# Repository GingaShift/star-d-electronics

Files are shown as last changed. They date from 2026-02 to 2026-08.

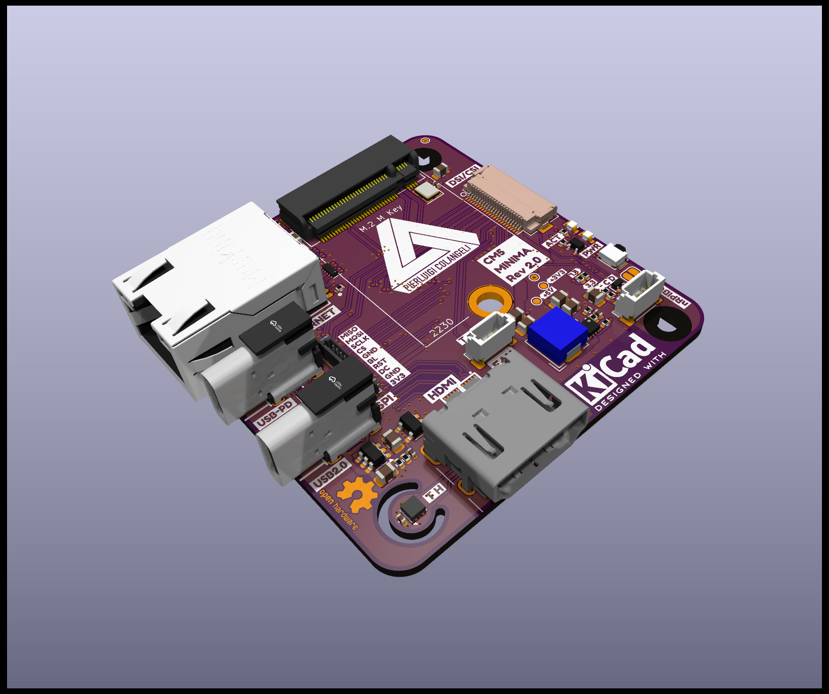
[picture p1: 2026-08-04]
AUTRE/CM5_MINIMA_REV2-main/CM5_MINIMA_REV2-main/PICS/SIDE.png

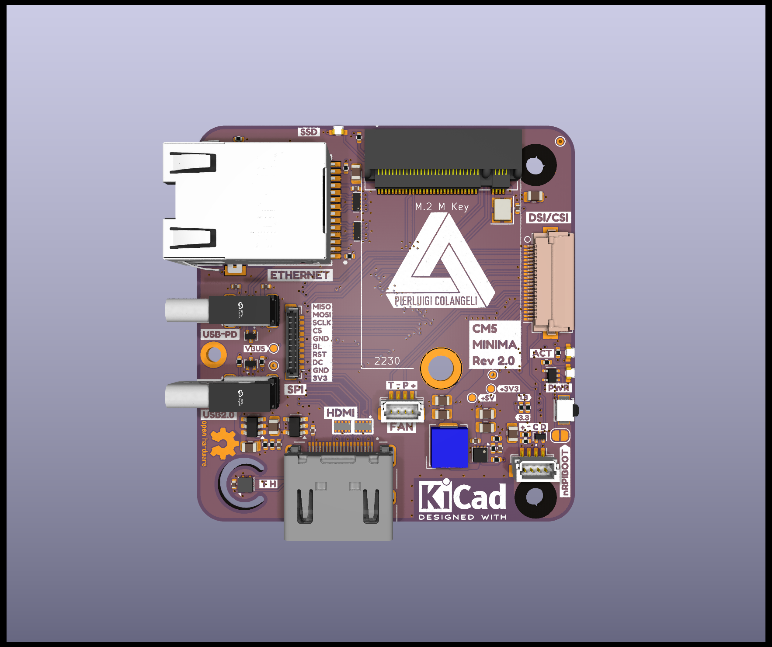
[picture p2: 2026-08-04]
AUTRE/CM5_MINIMA_REV2-main/CM5_MINIMA_REV2-main/PICS/F.png

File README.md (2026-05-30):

# STAR-D Electronics

Electronics repository for the STAR-D (Space Test of Amoeba Response - Dictyostelium) experiment developed within the ESA REXUS/BEXUS programme.

The electronics architecture is divided into several dedicated boards responsible for power conversion, experiment control, imaging, sensing, actuation and illumination.

---

# System Overview

The STAR-D electronics system is organized around:

- Power Board
- Main Control Board
- 5V Distribution Board
- CM5 Imaging System
- Microscope LED Board
- External Sensor Interfaces

---

# Power Board

## Purpose

Interfaces directly with the REXUS Service Module.

Responsibilities:

- 28V input from REXUS
- Power conversion
- Signal isolation
- RS422 communications
- Power distribution to the experiment

## PCB

Power_Board_F
Power_Board_B

## Main Components

- DC/DC Converters
- Optocouplers
- RS422 Transceiver
- D-SUB Interface
- Protection circuitry

---

# Main Control Board

## Purpose

Central controller of the experiment.

Responsibilities:

- Sensor acquisition
- Heater control
- Fluidic control
- Experiment sequencing
- Telemetry generation

## PCB

Main_Board
Main_Board_B

## Main Components

- ESP32-S3
- MAX31865
- PT100 Interface
- LSM6DSM
- ABP Pressure Sensor Interface
- SLF3S Flow Sensor Interface
- Actuator Drivers

---

# 5V Distribution Board

## Purpose

Dedicated power distribution board for high-current 5V subsystems.

Responsibilities:

- CM5 power supply

## PCB

5V_Board_F
5V_Board_B

---

# CM5 Imaging System

## Purpose

Scientific image acquisition and storage.

Responsibilities:

- Microscope control
- Camera acquisition
- Data storage
- Image processing

## PCB



## Main Components

- Raspberry Pi CM5
- NVMe SSD
- CSI Camera Interface

---

# Microscope LED PCB

## Purpose

Microscope illumination.

Responsibilities:

- Brightfield illumination
- Fluorescence illumination

## PCB

M_led

---

# External BME280 Board

## Purpose

Environmental monitoring outside the Pressure Vessel.

## PCB

External_BME_F
External_BME_B

---

# Repository Structure

```text
Documentation/
├── SED
├── Part_Listing
├── ICD
└── Images

Power_Board/

Main_Board/

5V_Board/

CM5_System/

Microscope_LED_PCB/

BME280_External/
```

---

# Documentation

Useful documents:

- STAR-D SED
- REXUS ICD
- Global Part Listing
- Power Board Part Listing
- Test Reports
- Integration Documents

---

# Team

STAR-D Electronics Team

Electronic Lead:
**Eden Elfassy**

ESA REXUS/BEXUS Programme

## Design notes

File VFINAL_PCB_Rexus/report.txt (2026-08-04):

Fichier placement: 'C:\Users\elfde\Desktop\STAR-D ELECTRONICS\VFINAL_PCB_Rexus\Main_PCB_STAR_D-all-pos.csv'.
Info: Nombre de composants: 120.
Info: Fini.

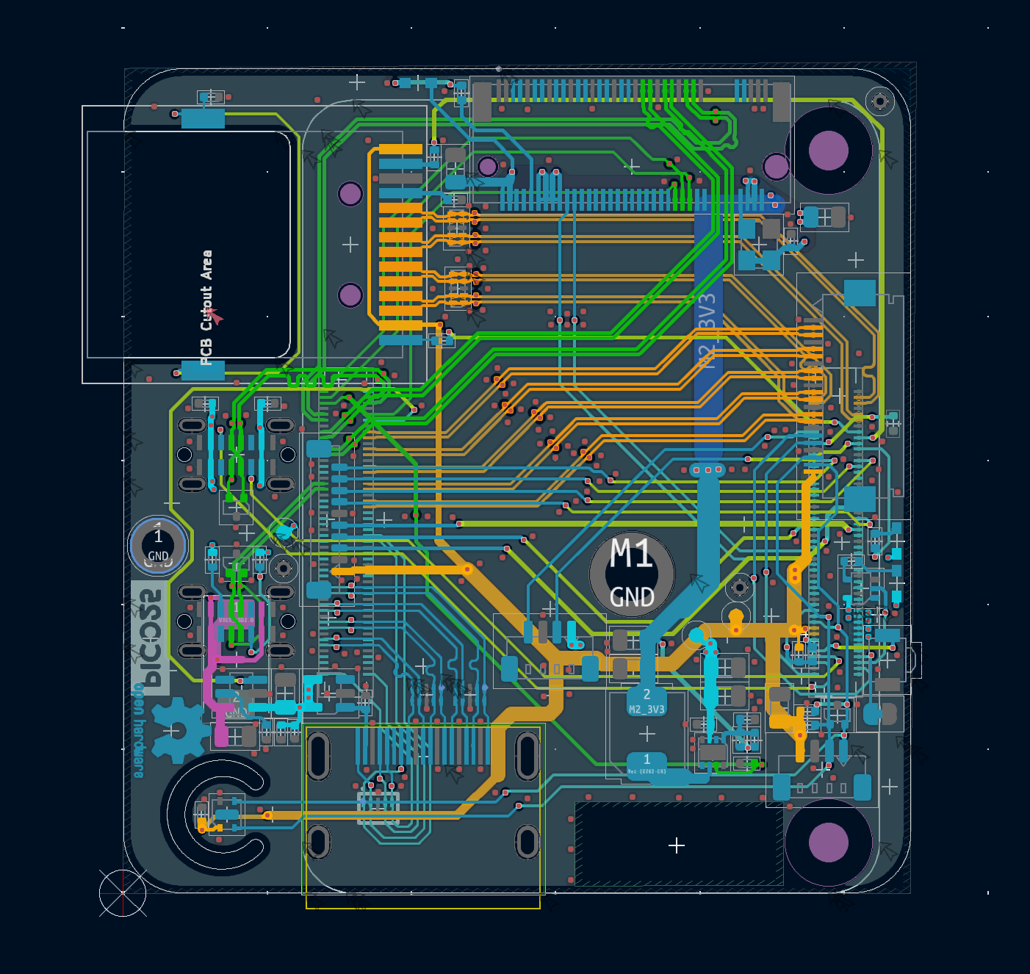
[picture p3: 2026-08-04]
AUTRE/CM5_MINIMA_REV2-main/CM5_MINIMA_REV2-main/PICS/PCB.png

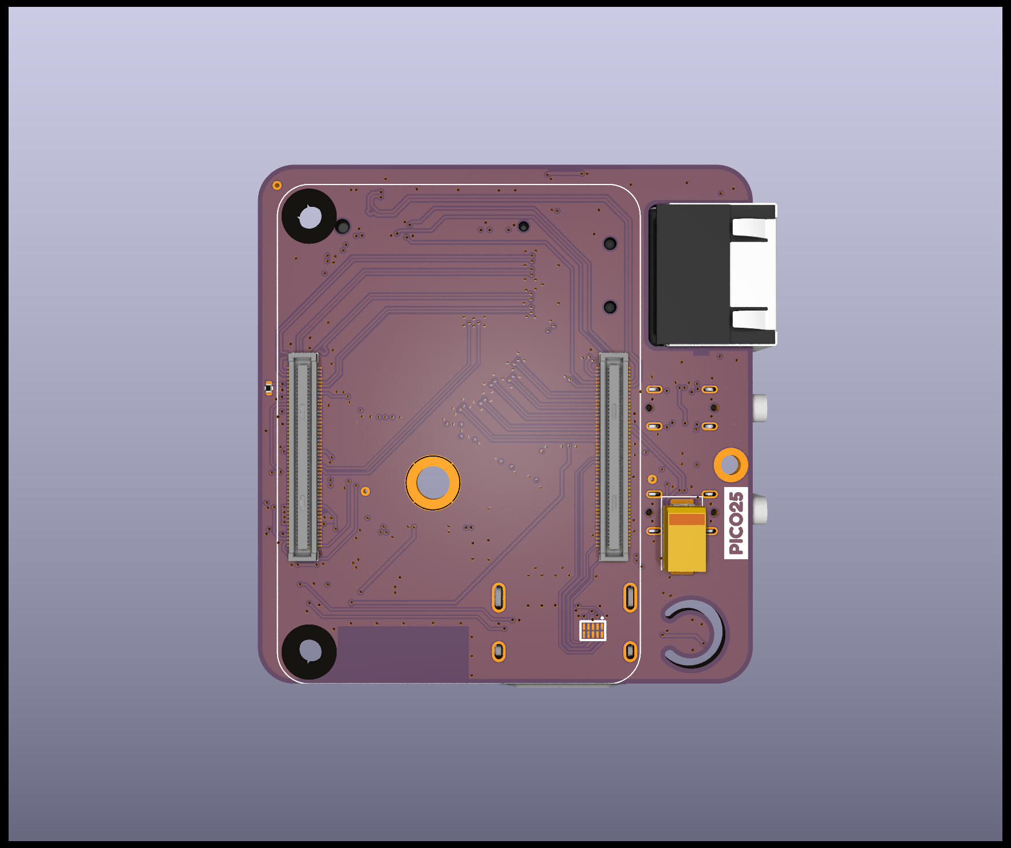
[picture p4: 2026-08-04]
AUTRE/CM5_MINIMA_REV2-main/CM5_MINIMA_REV2-main/PICS/B.png

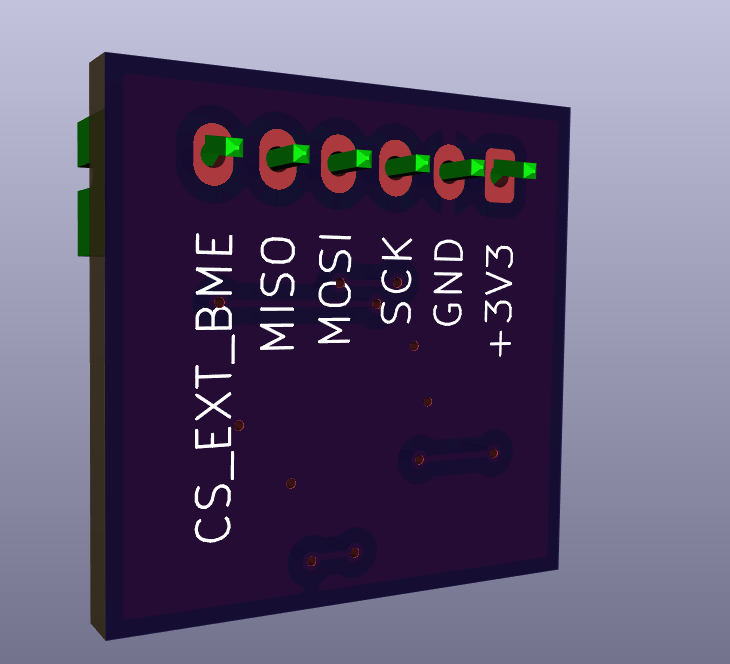
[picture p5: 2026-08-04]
Pics PCBs/External_BME_B.png

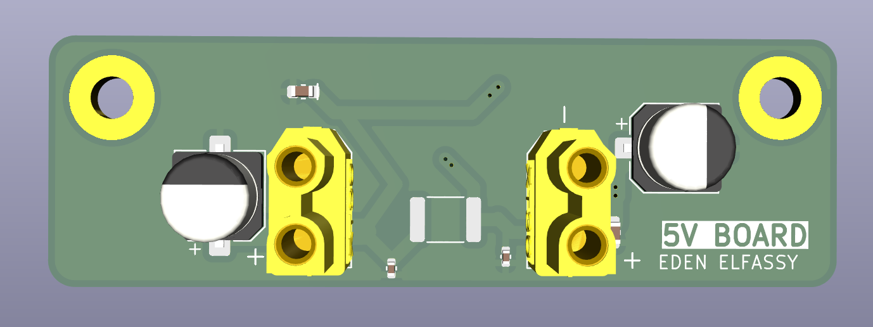
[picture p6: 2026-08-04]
Pics PCBs/5V_Board_F.png

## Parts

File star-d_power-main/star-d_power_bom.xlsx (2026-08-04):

Reference | Qty | Value | Footprint | Manufacturer Name | Comment
C1_1,C1_2,C1_3,C1_4,C1_5,C1_6,C1_7,C1_8,C1_9,C1_10,C1_11,C1_12,C1_13,C1_14,C1_15,C1_16,C1_17,C1_18 | 18 | 4.7uF | Capacitor_SMD:C_1206_3216Metric | Murata | GRM31CR71H475KA12L
C2_1,C2_2,C2_3 | 3 | 8200pF | Capacitor_SMD:C_0603_1608Metric | Vishay | VJ0603Y822KXAAC
C3_1,C3_2,C3_3 | 3 | 4.7uF | Capacitor_SMD:C_0603_1608Metric | Murata | GRM188Z71A475ME15D
C4_1,C4_2,C4_3,CD_1,CD_2 | 5 | 100nF | Capacitor_SMD:C_0603_1608Metric | KEMET | C0603C104K3RAC7411
C5_1,C5_2,C5_3,C5_4,C5_5,C5_6 | 6 | 47uF | Capacitor_SMD:C_1210_3225Metric | Murata | GRM32ER71A476KE15L
C5_7,C5_8,C5_9 | 3 | 47uF | Capacitor_SMD:C_2220_5750Metric | TDK | CGA9N3X7R1E476M230KB
CF1 | 1 | 1uF | Capacitor_SMD:C_1206_3216Metric | TDK | C3216X7R1H105K160AB
CFT1,CFT2,CFT3,CFT4 | 4 | C_Feedthrough | NFM18CC221R1C3D:NFM18CC101R1C3D | Murata | NFM18CC221R1C3D
D1,D2,D3 | 3 | LED | LED_SMD:LED_0603_1608Metric | LITEON | LTST-C191KFKT
FL1 | 1 | Common Mode Choke 215uH | PA2754NL:PA2754NL | Pulse Electronics | PA2754NL
IC1,IC2,IC3 | 3 | MAX17639AFN+ | MAX17639AFN+:MAX17793AFN | Analog Devices | MAX17639AFN+
J1 | 1 | 3.3V connector | Connector_AMASS:AMASS_XT30PW-F_1x02_P2.50mm_Horizontal | AMASS | XT30PW-F
J2 | 1 | 5V connector | Connector_AMASS:AMASS_XT30PW-F_1x02_P2.50mm_Horizontal | AMASS | XT30PW-F
J3 | 1 | 7V connector | Connector_AMASS:AMASS_XT30PW-F_1x02_P2.50mm_Horizontal | AMASS | XT30PW-F
J4 | 1 | D-sub input | LD15P33E4GX00LF:AMPHENOL_LD15P33E4GX00LF | Amphenol | LD15P33E4GX00LF
J5 | 1 | D-sub output | LD15P33E4GX00LF:AMPHENOL_LD15P33E4GX00LF | Amphenol | LD15P33E4GX00LF
L1_1 | 1 | 2.2uH | XGL1010-222MED:IND_XGL1010-222MED | Coilcraft | XGL1010-222MED
L1_2,L1_3 | 2 | 3.3uH | XGL1010-222MED:IND_XGL1010-222MED | Coilcraft | XGL1010-332MED
LF1 | 1 | 100uH | SRP2313AA-101M:INDPM235220X1300N | Bourns | SRP2313AA-101M
R1_1,R1_2,R1_3 | 3 | 3.32M | Resistor_SMD:R_0603_1608Metric | Vishay | CRCW06033M32FKEA
R2_1 | 1 | 1.5M | Resistor_SMD:R_0603_1608Metric | Vishay | CRCW06031M50FKEA
R2_2 | 1 | 825k | Resistor_SMD:R_0603_1608Metric | Vishay | CRCW0603825KFKEA
R2_3 | 1 | 604k | Resistor_SMD:R_0603_1608Metric | Vishay | CRCW0603604KFKEA
R3_1 | 1 | 158k | Resistor_SMD:R_0603_1608Metric | Vishay | CRCW0603158KFKEA
R3_2 | 1 | 249k | Resistor_SMD:R_0603_1608Metric | Vishay | CRCW0603249KFKEA
R3_3 | 1 | 105k | Resistor_SMD:R_0603_1608Metric | Vishay | CRCW0603105KFKEA
R4_1 | 1 | 34.8k | Resistor_SMD:R_0603_1608Metric | Vishay | CRCW060334K8FKEA
R4_2 | 1 | 34k | Resistor_SMD:R_0603_1608Metric | Vishay | CRCW060334K0FKEA
R4_3 | 1 | 9.76k | Resistor_SMD:R_0603_1608Metric | Vishay | CRCW06039K76FKEA
R5_1,R5_2,R5_3 | 3 | 75k | Resistor_SMD:R_0603_1608Metric | Vishay | CRCW060375K0FKEA
R6_1,R6_2,R6_3 | 3 | 20k | Resistor_SMD:R_0603_1608Metric | Vishay | CRCW060320K0FKEA
RLED_1,RO1,RO3,RO5 | 4 | 1k | Resistor_SMD:R_0603_1608Metric | Panasonic | ERJ-PA3J102V
RLED_2 | 1 | 604R | Resistor_SMD:R_0603_1608Metric | Panasonic | ERJ-PA3D6040V
RLED_3 | 1 | 261R | Resistor_SMD:R_0603_1608Metric | Panasonic | ERJ-PA3F2610V
RO2,RO4,RO6 | 3 | 3k3 | Resistor_SMD:R_0603_1608Metric | Panasonic | ERJ-PA3J332V
U1,U2,U3 | 3 | VO615A-4 | Package_DIP:DIP-4_W10.16mm | Vishay | VO615A-4
U4 | 1 | BME280 | Package_LGA:Bosch_LGA-8_2.5x2.5mm_P0.65mm_ClockwisePinNumbering | Bosch | BME280

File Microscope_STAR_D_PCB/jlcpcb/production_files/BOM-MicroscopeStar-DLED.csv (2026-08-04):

Comment | Designator | Footprint | LCSC | Quantity
180R | R1,R2,R3,R4 | R_0402_1005Metric | C138045 | 4
Conn_01x03_Socket | J1 | Molex_Micro-Fit_3.0_43650-0312_1x03-1MP_P3.00mm_Horizontal | C114109 | 1
KT-0603-W | D1,D2,D3,D4 | LED_0603_1608Metric | C5973179 | 4
SI2302B-TP | Q1 | SOT95P237X125-3N | C52117627 | 1

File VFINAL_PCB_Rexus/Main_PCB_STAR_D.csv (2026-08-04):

Reference | Qty | Value | DNP | Exclude from BOM | Exclude from Board | Footprint | Datasheet
AE1 | 1 | Antenna_Chip |  |  |  | Connector_Coaxial:U.FL_Molex_MCRF_73412-0110_Vertical
C1,C6,C10 | 3 | 1uF 0402 |  |  |  | Capacitor_SMD:C_0402_1005Metric
C2,C4 | 2 | 12pF 0402 |  |  |  | Capacitor_SMD:C_0402_1005Metric
C3 | 1 | 10uF 0402 |  |  |  | Capacitor_SMD:C_0402_1005Metric
C5,C7,C9,C15,C17,C18,C19,C20,C21,C22,C24,C27,C30,C33,C34,C35 | 16 | 100nF 0402 |  |  |  | Capacitor_SMD:C_0402_1005Metric
C8 | 1 | 10nF 0402 |  |  |  | Capacitor_SMD:C_0402_1005Metric
C11,C13 | 2 | 0.1uF 0402 |  |  |  | Capacitor_SMD:C_0402_1005Metric
C12 | 1 | 10nF 0603 |  |  |  | Capacitor_SMD:C_0402_1005Metric
C14 | 1 | 15pF 0402 |  |  |  | Capacitor_SMD:C_0402_1005Metric
C16 | 1 | 2.2uF 0603 |  |  |  | Capacitor_SMD:C_0402_1005Metric
C23,C28,C31,C32 | 4 | 10uF 0603 |  |  |  | Capacitor_SMD:C_0603_1608Metric
C25,C26 | 2 | 0.1uF |  |  |  | Capacitor_SMD:C_0402_1005Metric
C29 | 1 | 100nF |  |  |  | Capacitor_SMD:C_0402_1005Metric
D1 | 1 | MBR0520 |  |  |  | Diode_SMD:D_SOD-123 | http://www.mccsemi.com/up_pdf/MBR0520~MBR0580(SOD123).pdf
D2,D3,D4 | 3 | KT-0805Y |  |  |  | LED_SMD:LED_0805_2012Metric
IC1 | 1 | MAX31865ATP+ |  |  |  | MAX31865ATP+:QFN65P500X500X80-21N | https://www.analog.com/MAX31865/datasheet
IC2 | 1 | W25Q01JVZEIQ |  |  |  | Package_SON:WSON-8-1EP_6x5mm_P1.27mm_EP3.4x4.3mm | https://www.winbond.com/hq/search-resource-file.jsp?partNo=W25Q01JVZEIQ&type=datasheet
IC3 | 1 | ISL83491IBZ-T |  |  |  | ISL83491IBZ-T:SOIC127P600X175-14N | https://www.renesas.com/en-us/www/doc/datasheet/isl83483-85-88-90-91.pdf
IC4 | 1 | DRV8834PWP |  |  |  | DRV8834PWP:SOP65P640X120-25N | https://datasheet.datasheetarchive.com/originals/distributors/Datasheets-SFU2/DSASFU100034685.pdf
IC5 | 1 | ULN2003ADR |  |  |  | ULN2003ADR:SOIC127P600X175-16N | http://www.ti.com/lit/ds/symlink/uln2003a.pdf
J1 | 1 | Conn_01x05_Pin |  |  |  | Connector_JST:JST_EH_S5B-EH_1x05_P2.50mm_Horizontal
J2 | 1 | Conn_01x09 |  |  |  | Connector_JST:JST_GH_BM09B-GHS-TBT_1x09-1MP_P1.25mm_Vertical
J3 | 1 | Conn_01x04_Pin |  |  |  | Connector_JST:JST_EH_S4B-EH_1x04_P2.50mm_Horizontal
J4,J7 | 2 | Conn_01x06_Pin |  |  |  | Connector_JST:JST_EH_S6B-EH_1x06_P2.50mm_Horizontal
J5 | 1 | Conn_01x04 |  |  |  | Connector_JST:JST_PH_S4B-PH-K_1x04_P2.00mm_Horizontal
J6,J12,J13,J15,J_HEATER1,J_HEATER2,J_HEATER3,J_HEATER4 | 8 | Conn_01x02_Pin |  |  |  | Connector_AMASS:AMASS_XT30U-F_1x02_P5.0mm_Vertical
J8 | 1 | Conn_01x02 |  |  |  | Connector_JST:JST_EH_S2B-EH_1x02_P2.50mm_Horizontal
J9 | 1 | Conn_01x05 |  |  |  | Connector_JST:JST_XH_B5B-XH-A_1x05_P2.50mm_Vertical
J10 | 1 | TYPE-C 16PIN 2MD(073) |  |  |  | Connector_USB:USB_C_Receptacle_GCT_USB4105-xx-A_16P_TopMnt_Horizontal | https://www.usb.org/sites/default/files/documents/usb_type-c.zip
J11 | 1 | Conn_01x03 |  |  |  | Connector_JST:JST_EH_S3B-EH_1x03_P2.50mm_Horizontal
L1 | 1 | 2.0nH 0402 |  |  |  | Inductor_SMD:L_0402_1005Metric
L3 | 1 | 4.7nH 0402 |  |  |  | Inductor_SMD:L_0402_1005Metric
Q7,Q8,Q9,Q10 | 4 | IRLML6344TRPBF |  |  |  | IRLML6344TRPBF:SOT95P237X112-3N | https://www.infineon.com/dgdl/irlml6344pbf.pdf?fileId=5546d462533600a4015356689c44262c
R1,R5,R12 | 3 | 10kR 0402 |  |  |  | Resistor_SMD:R_0402_1005Metric
R2 | 1 | 2R 0402 |  |  |  | Resistor_SMD:R_0402_1005Metric
R3 | 1 | 47kR 0402 |  |  |  | Resistor_SMD:R_0402_1005Metric
R4,R_ADC_POT1 | 2 | 1kR 0402 |  |  |  | Resistor_SMD:R_0402_1005Metric
R6,R8 | 2 | 51kR 0402 |  |  |  | Resistor_SMD:R_0402_1005Metric
R7 | 1 | 400R 0402 |  |  |  | Resistor_SMD:R_0402_1005Metric
R9,R11 | 2 | 0.2R 1206 |  |  |  | Resistor_SMD:R_0402_1005Metric
R10 | 1 | 120R 0402 |  |  |  | Resistor_SMD:R_0402_1005Metric
R13 | 1 | 22kR 0402 |  |  |  | Resistor_SMD:R_0402_1005Metric
R14,R15 | 2 | 5.1kR 0402 |  |  |  | Resistor_SMD:R_0402_1005Metric
R16,R17 | 2 | 22R 0402 |  |  |  | Resistor_SMD:R_0402_1005Metric
R18,R19 | 2 | 2kR 0402 |  |  |  | Resistor_SMD:R_0402_1005Metric
R_G1,R_G2,R_G3,R_G4 | 4 | 100R 0402 |  |  |  | Resistor_SMD:R_0402_1005Metric
R_I2C_SCL1,R_I2C_SCL2 | 2 | 4K7 0402 |  |  |  | Resistor_SMD:R_0402_1005Metric
R_PD1,R_PD2,R_PD3,R_PD4 | 4 | 100kR 0402 |  |  |  | Resistor_SMD:R_0402_1005Metric
SW1,SW2 | 2 | SW_SPST |  |  |  | Button_Switch_SMD:SW_Tactile_SPST_NO_Straight_CK_PTS636Sx25SMTRLFS
TP1,TP2,TP3,TP4,TP5,TP6,TP7,TP8,TP9,TP10,TP11,TP12,TP13,TP14,TP15,TP16,TP18 | 17 | TestPoint |  |  |  | TestPoint:TestPoint_Pad_1.0x1.0mm
U1 | 1 | ESP32-S3 |  |  |  | Package_DFN_QFN:QFN-56-1EP_7x7mm_P0.4mm_EP4x4mm | https://www.espressif.com/sites/default/files/documentation/esp32-s3_datasheet_en.pdf
U2 | 1 | BME280 |  |  |  | Package_LGA:Bosch_LGA-8_2.5x2.5mm_P0.65mm_ClockwisePinNumbering | https://www.bosch-sensortec.com/media/boschsensortec/downloads/datasheets/bst-bme280-ds002.pdf
U4 | 1 | LSM6DSM |  |  |  | Package_LGA:LGA-14_3x2.5mm_P0.5mm_LayoutBorder3x4y | https://www.st.com/resource/en/datasheet/lsm6dsm.pdf
Y1 | 1 | 40MHz 3225 9pF |  |  |  | Crystal:Crystal_SMD_3225-4Pin_3.2x2.5mm

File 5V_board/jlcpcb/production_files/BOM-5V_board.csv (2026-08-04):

Comment | Designator | Footprint | LCSC | Quantity
100nF 0402 | C33,C34 | C_0402_1005Metric | C307331 | 2
10uF 0603 | C31,C32 | C_0603_1608Metric | C96446 | 2
470µF | C35,C_CM5_BULK1 | CP_Elec_6.3x7.7 | C3354 | 2
Conn_01x02_Pin | J13,J15 | Molex_Micro-Fit_3.0_43650-0215_1x02_P3.00mm_Vertical | C293740 | 2
Conn_01x04 | J1 | Molex_Micro-Latch_53253-0470_1x04_P2.00mm_Vertical | C504808 | 1

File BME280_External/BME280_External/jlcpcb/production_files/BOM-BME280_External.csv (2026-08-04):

Comment | Designator | Footprint | LCSC | Quantity
0.1uF | C1,C2 | C_0402_1005Metric | C141382 | 2
BME280 | U1 | Bosch_LGA-8_2.5x2.5mm_P0.65mm_ClockwisePinNumbering | C92489 | 1
Conn_01x06_Pin | J1 | Molex_Micro-Latch_53253-0670_1x06_P2.00mm_Vertical | C564034 | 1

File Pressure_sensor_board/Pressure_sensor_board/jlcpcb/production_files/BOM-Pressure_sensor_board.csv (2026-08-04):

Comment | Designator | Footprint | LCSC | Quantity
100nF 0603 | C1 | C_0603_1608Metric | C24452 | 1
Conn_01x05 | J1 | Molex_Micro-Latch_53254-0570_1x05_P2.00mm_Horizontal | C585950 | 1
ABPDANV015PGSA3 | IC1 | ABPDANV015PGSA3 |  | 1

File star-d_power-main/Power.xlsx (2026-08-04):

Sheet: Folha1
VIN | 28 | V |  | D | 0.25
VOUT | 7 | V |  | CIN | 49.34210526 | uF
fSW | 400000 | Hz |  | L | 3.645833333 | uH |  | LSEL | 6.8 | uH
DeltaVIN | 0.1 | V |  | tresponse | 7e-06
eff | 0.95 |  |  | COUT | 87.5 | uF |  | COUTSEL | 111 | uF
IOUTMAX | 10 | A |  | CSS | 8200 | pF
K | 4.8 |  |  | RUVLBOT | 605.8394161 | kR
fc | 50000 | Hz |  | RFBTOP | 104.1441441 | kR | 104
ISTEP | 5 | A |  | RFBBOT | 9.763513514 | kR
DeltaVOUT | 0.2 | V
RUVLTOP | 3.32 | MR
VENR | 1.25 | V |  | RFBTOP | 105
VINU | 8.1 | V |  | RFBBOT | 9.76
 |  |  |  | VOUT | 7.054918033
 |  |  |  |  | 98.34 | 158 | 1.606670734
 |  |  |  |  | 134.16 | 249 | 1.855992844
 |  |  |  |  | 104 | 176.8
 |  |  | 3.142857143 |  | 33.81147541

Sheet: Folha2
Designator | Amount | R/L/C | V min | Others | Component | Size | Link | Price/un | Total/PCB
IC[1..3] | 3 |  |  |  | MAX17639AFN+ |  | https://www.mouser.fr/ProductDetail/Analog-Devices-Maxim-Integrated/MAX17639AFN+ | 8.13 € | 80.15 €
R1_[1..3] | 3 | 3.32 Mohm |  |  | CRCW06033M32FKEA | 0603 | https://www.mouser.fr/ProductDetail/Vishay/CRCW06033M32FKEA | 0.09 €
R2_1 | 1 | 1.5 Mohm |  |  | CRCW06031M50FKEA | 0603 | https://www.mouser.fr/ProductDetail/Vishay/CRCW06031M50FKEA | 0.09 €
R2_2 | 1 | 825 kohm |  |  | CRCW0603825KFKEA | 0603 | https://www.mouser.fr/ProductDetail/Vishay/CRCW0603825KFKEA?qs=p2bJuJLPpvQJv%252BSX6BCMUg%3D%3D | 0.09 €
R2_3 | 1 | 604 kohm |  |  | CRCW0603604KFKEA | 0603 | https://www.mouser.fr/ProductDetail/Vishay/CRCW0603604KFKEA?qs=ze%252BM7jRK1VYKCr%2Fok50BCw%3D%3D | 0.09 €
R3_1 | 1 | 158 kohm |  |  | CRCW0603158KFKEA | 0603 | https://www.mouser.fr/ProductDetail/Vishay/CRCW0603158KFKEA?qs=5N7VPDfziMSpEbCL%252B8rPOw%3D%3D | 0.09 €
R3_2 | 1 | 249 kohm |  |  | CRCW0603249KFKEA | 0603 | https://www.mouser.fr/ProductDetail/Vishay/CRCW0603249KFKEA?qs=mhqxD2tmD97uUS1nIJhakQ%3D%3D | 0.09 €
R3_3 | 1 | 105 kohm |  |  | CRCW0603105KFKEA | 0603 | https://www.mouser.fr/ProductDetail/Vishay/CRCW0603105KFKEA?qs=l1I5L%2FyVolijl%252Bqg9cSIKQ%3D%3D | 0.09 €
R4_1 | 1 | 34.8 kohm |  |  | CRCW060334K8FKEA | 0603 | https://www.mouser.fr/ProductDetail/Vishay/CRCW060334K8FKEA?qs=68g8TF7PocIAjJxcXJVf9g%3D%3D | 0.09 €
R4_2 | 1 | 34 kohm |  |  | CRCW060334K0FKEA | 0603 | https://www.mouser.fr/ProductDetail/Vishay/CRCW060334K0FKEA?qs=9%2FCyznrMg3XHBoGG%2FQg7oQ%3D%3D | 0.09 €
R4_3 | 1 | 9.76 kohm |  |  | CRCW06039K76FKEA | 0603 | https://www.mouser.fr/ProductDetail/Vishay/CRCW06039K76FKEA?qs=yf2sAwiRN649TjJ%2FhlEI1Q%3D%3D | 0.09 €
R5_[1..3] | 3 | 75 kohm |  |  | CRCW060375K0FKEA | 0603 | https://www.mouser.fr/ProductDetail/Vishay/CRCW060375K0FKEA?qs=rTzW0HAgjYM2sBnUIlegvw%3D%3D | 0.09 €
R6_[1..3] | 3 | 20 kohm |  |  | CRCW060320K0FKEA | 0603 | https://www.mouser.fr/ProductDetail/Vishay/CRCW060320K0FKEA?qs=QZuYiDxzHajCQLs7n6RwKw%3D%3D | 0.09 €
RLED_1 | 1 | 1 kohm |  |  | ERJ-PA3J102V | 0603 | https://www.mouser.fr/ProductDetail/Panasonic/ERJ-PA3J102V?qs=BzJM0faLVqWUoK2brnXytQ%3D%3D | 0.10 €
RLED_2 | 1 | 604 ohm |  |  | ERJ-PA3D6040V | 0603 | https://www.mouser.fr/ProductDetail/Panasonic/ERJ-PA3D6040V?qs=BzJM0faLVqVr6j5%252BuCH0wQ%3D%3D | 0.21 €
RLED_3 | 1 | 261 ohm |  |  | ERJ-PA3F2610V | 0603 | https://www.mouser.fr/ProductDetail/Panasonic/ERJ-PA3F2610V?qs=BzJM0faLVqWOtl0KpXWkew%3D%3D | 0.12 €
L1 | 1 | 2.2 uH | 3.3V |  | XGL1010-222MED |  | https://www.digikey.fr/en/products/detail/coilcraft/XGL1010-222MED/21387621?s=N4IgTCBcDaIBoHEAyBGADOgtGHBZAogCIgC6AvkA | 5.82 €
L[2,3] | 2 | 3.3 uH | 7V |  | XGL1010-332MED |  | https://www.digikey.fr/en/products/detail/coilcraft/XGL1010-332MED/21387582?s=N4IgTCBcDaIBoHEAyBGADOgtAZm2AsgKIAiIAugL5A | 5.82 €
C1_[1..18] | 18 | 4.7 uF | 28V | X7R | GRM31CR71H475KA12L | 1206 | https://www.digikey.de/de/products/detail/murata-electronics/GRM31CR71H475KA12L/2548209 | 0.27 €
C2_[1..3] | 3 | 8200 pF |  | X7R | VJ0603Y822KXAAC | 0603 | https://www.mouser.fr/ProductDetail/Vishay-Vitramon/VJ0603Y822KXAAC?qs=sGAEpiMZZMvsSlwiRhF8qsy6D4RIz3svHH6F26SGKQI%3D | 0.15 €
C3_[1..3] | 3 | 4.7 uF | 1.8V | X7R | GRM188Z71A475ME15D | 0603 | https://www.digikey.de/de/products/detail/murata-electronics/GRM188Z71A475ME15D/13904814 | 0.19 €
C4_[1..3], CD_[1,2] | 5 | 100 nF |  | X7R | C0603C104K3RAC7411 | 0603 | https://www.mouser.fr/ProductDetail/KEMET/C0603C104K3RAC7411?qs=sGAEpiMZZMvsSlwiRhF8qtMAW1uaXrptnL6k6SP7Y74%3D | 0.09 €
C5_[1..6] | 6 | 47 uF | 5V | X7R | GRM32ER71A476KE15L | 1210 | https://www.digikey.be/de/products/detail/murata-electronics/GRM32ER71A476KE15L/2039039 | 0.72 €
C5_[7..9] | 3 | 47 uF | 12V | X7R | CGA9N3X7R1E476M230KB | 2220 | https://www.mouser.de/ProductDetail/TDK/CGA9N3X7R1E476M230KB | 3.78 €
D[1..3] | 3 |  |  | LED | LTST-C191KFKT | 0603 | https://www.mouser.fr/ProductDetail/LITEON/LTST-C191KFKT?qs=sGAEpiMZZMv0DJfhVcWlKzPaVbnPffcwrhTtPymJX2Y%3D | 0.09 €
J[1..3] | 3 |  |  | horizontal power | 43650-0200 |  | https://www.mouser.fr/ProductDetail/Molex/43650-0200?qs=HlEFOAM0q6XGaAJJj3Pssw%3D%3D | 0.92 €
J4 | 1 |  |  | Dsub-15, right-angle, male | LD15P33E4GX00LF |  | https://www.mouser.fr/ProductDetail/Amphenol-Commercial-Products/LD15P33E4GX00LF?qs=tZOhSuJQg1lUHGna%252BrXX2w%3D%3D | 1.61 €
J5 | 1 |  |  | Dsub-15, right-angle, female | LD15S33E4GV00LF |  | https://www.mouser.fr/ProductDetail/Amphenol-Commercial-Products/LD15S33E4GV00LF?qs=tZOhSuJQg1mwdHXzYsS27Q%3D%3D | 1.74 €
FL1 | 1 | 215uH |  | CMC | PA2754NL |  | https://www.mouser.fr/ProductDetail/Pulse-Electronics/PA2754NL?qs=%252BUGZmmosPSIl0ME75doAGQ%3D%3D | 1.78 €
LF1 | 1 | 100uH |  |  | SRP2313AA-101M |  | https://www.mouser.fr/ProductDetail/Bourns/SRP2313AA-101M?qs=gZXFycFWdANfITbqx%252BPtOw%3D%3D | 5.67 €
CF1 | 1 | 1uF |  |  | C3216X7R1H105K160AB | 1206 | https://www.mouser.fr/ProductDetail/TDK/C3216X7R1H105K160AB | 0.10 €
CFT[1..4] | 4 | 220pF |  | feed-through | NFM18CC221R1C3D | 0603 | https://www.mouser.fr/ProductDetail/Murata-Electronics/NFM18CC221R1C3D?qs=0j%2FqW2fzXq8leLhxLw8kvg%3D%3D | 0.11 €

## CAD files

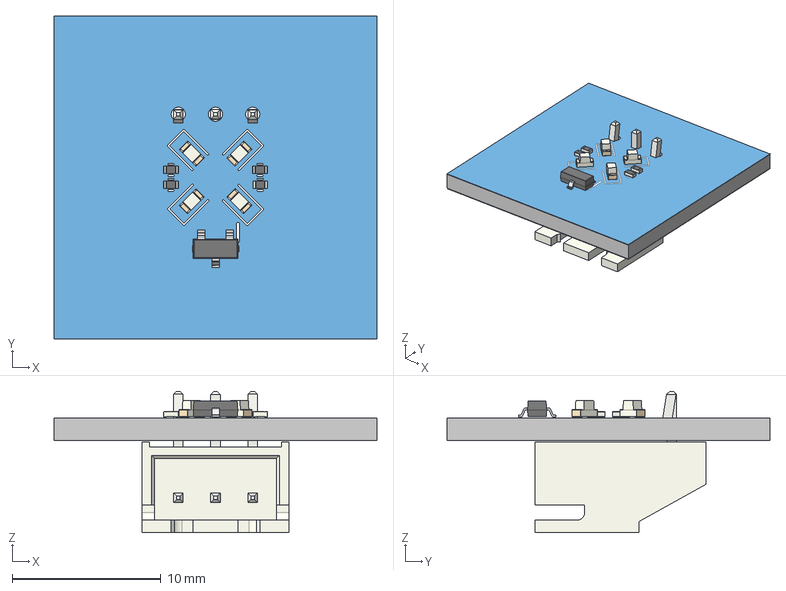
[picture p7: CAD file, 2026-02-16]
AUTRE/CAD_PCB/MicroscopeStar-DLED.step
21.7 x 21.7 x 9.50 mm
R_0402_1005Metric x 4
LED_0603_1608Metric x 4
��1
��2
JST_XH_S3B-XH-A_1x03_P2.50mm_Horizontal
MicroscopeStar-DLED_silkscreen
MicroscopeStar-DLED_soldermask
MicroscopeStar-DLED_PCB

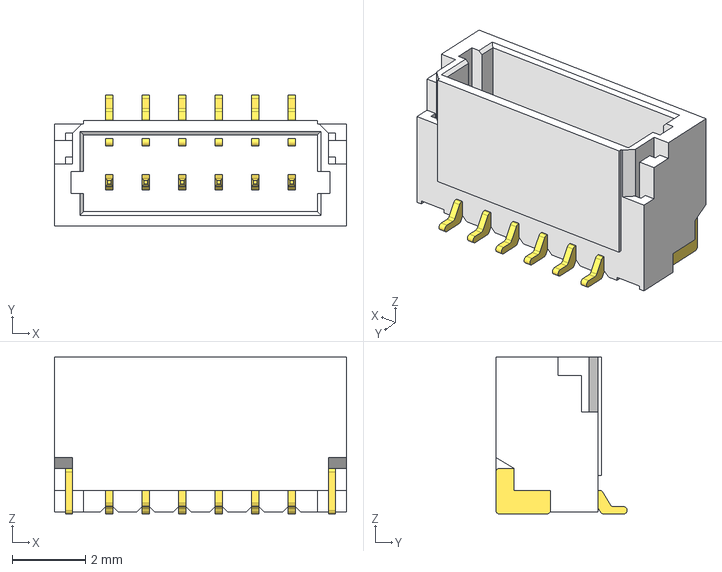
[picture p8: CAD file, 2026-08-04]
AUTRE/CM5_MINIMA_REV2-main/CM5_MINIMA_REV2-main/3d_lib/BM6B-SRSS-TB.step
8.00 x 3.60 x 4.30 mm

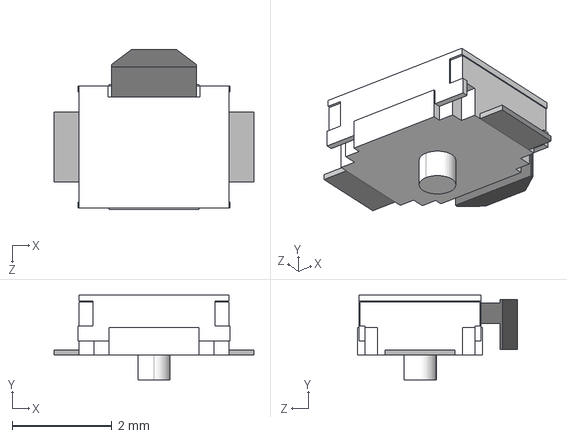
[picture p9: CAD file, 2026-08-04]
AUTRE/CM5_MINIMA_REV2-main/CM5_MINIMA_REV2-main/3d_lib/LIB_B3U-3000PM-B/B3U-3000PM-B/3D/B3U-3000PM-B.stp
4.00 x 1.70 x 3.20 mm

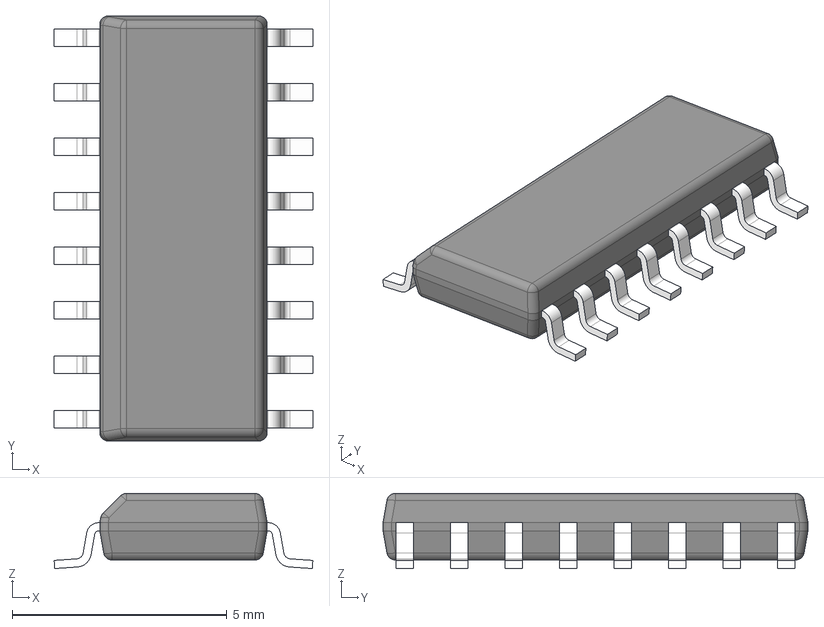
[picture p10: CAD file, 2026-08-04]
AUTRE/CM5_MINIMA_REV2-main/CM5_MINIMA_REV2-main/ULN2003ADR/ULN2003ADR.stp
6.03 x 9.90 x 1.75 mm
BODY-SO
LEAD-SO x 16
PIN1-ID

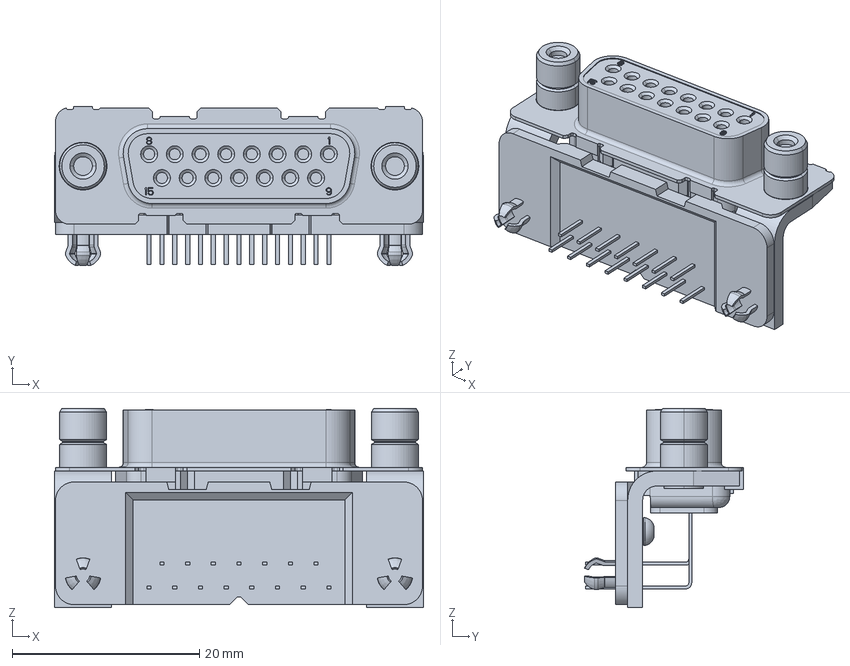
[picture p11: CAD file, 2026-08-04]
AUTRE/Sans_heater_VFINAL_PCB_Rexus/importations/3-106506-2/3-106506-2.stp
39.4 x 16.9 x 21.3 mm

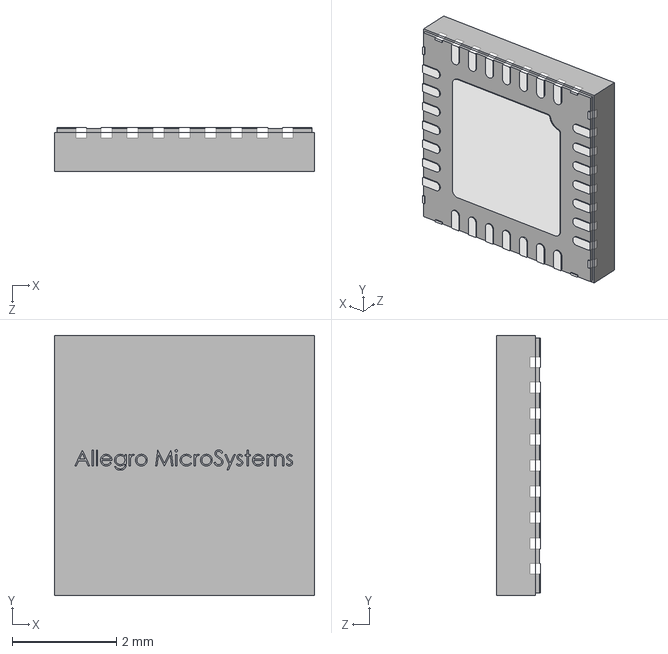
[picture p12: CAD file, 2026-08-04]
AUTRE/Sans_heater_VFINAL_PCB_Rexus/importations/A4988SETTR-T/A4988SETTR-T.stp
5.00 x 5.00 x 0.855 mm

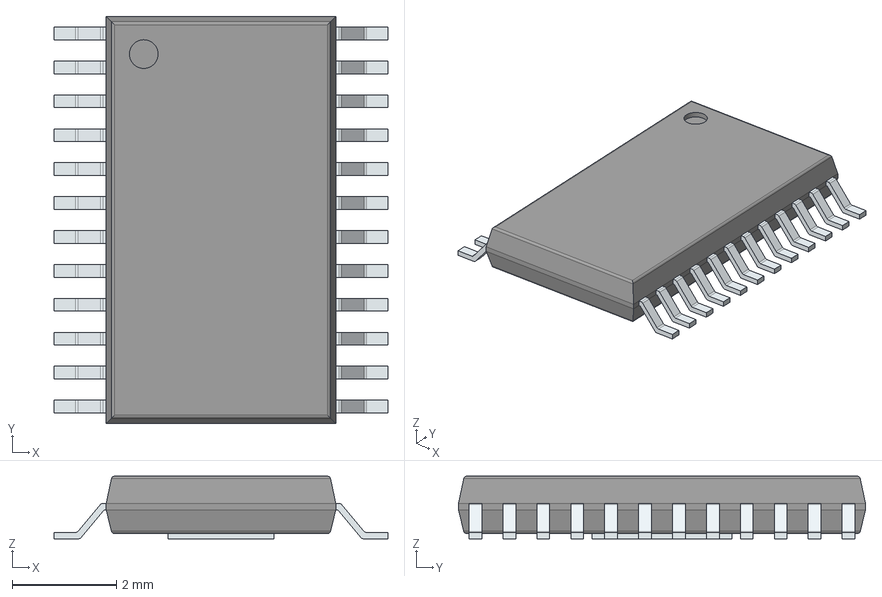
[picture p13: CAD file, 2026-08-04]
AUTRE/Sans_heater_VFINAL_PCB_Rexus/importations/DRV8834PWP/DRV8834PWP.stp
6.40 x 7.80 x 1.20 mm
PinsArrayLR
ThermalPad

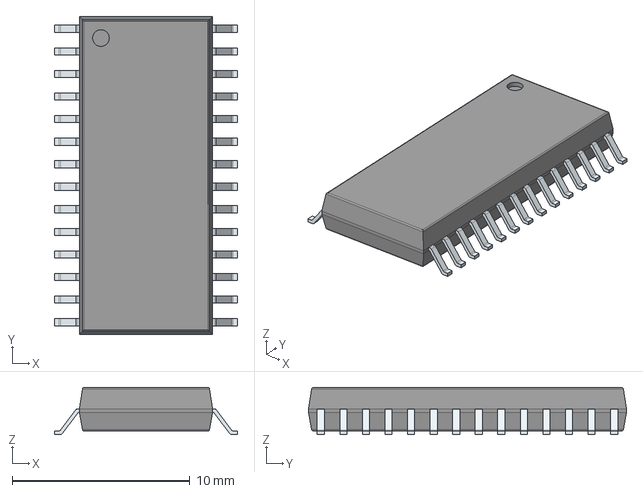
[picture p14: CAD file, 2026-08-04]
AUTRE/Sans_heater_VFINAL_PCB_Rexus/importations/MCP23S17-E_SO/MCP23S17-E_SO.stp
10.3 x 17.9 x 2.65 mm
PinsArrayLR

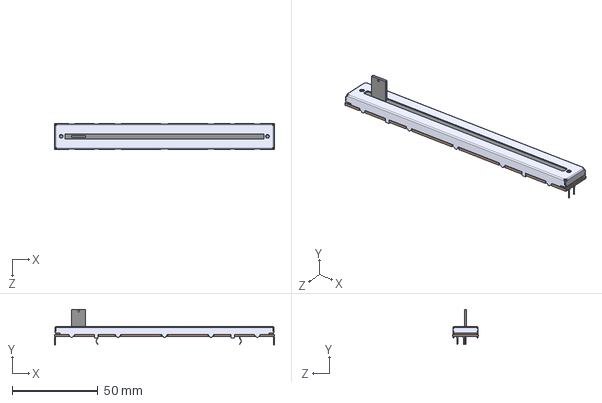
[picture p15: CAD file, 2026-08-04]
AUTRE/Sans_heater_VFINAL_PCB_Rexus/importations/PTB0143-2010BPA103/PTB0143-2010BPA103.stp
128.0 x 20.4 x 15.0 mm

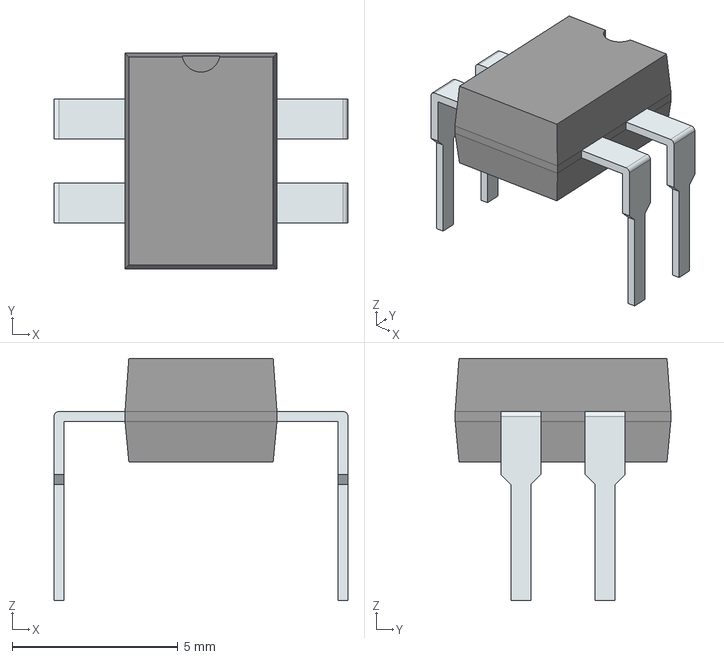
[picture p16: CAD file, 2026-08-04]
AUTRE/Sans_heater_VFINAL_PCB_Rexus/importations/VO615A-4/VO615A-4.stp
8.86 x 6.50 x 7.30 mm
PinsArrayLR

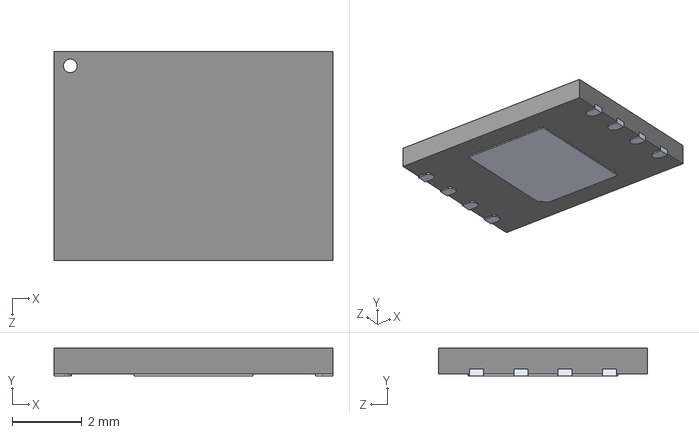
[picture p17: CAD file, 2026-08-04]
AUTRE/Sans_heater_VFINAL_PCB_Rexus/importations/W25Q01JVZ/W25Q01JVZEIQ.stp
8.00 x 0.8 x 6.00 mm

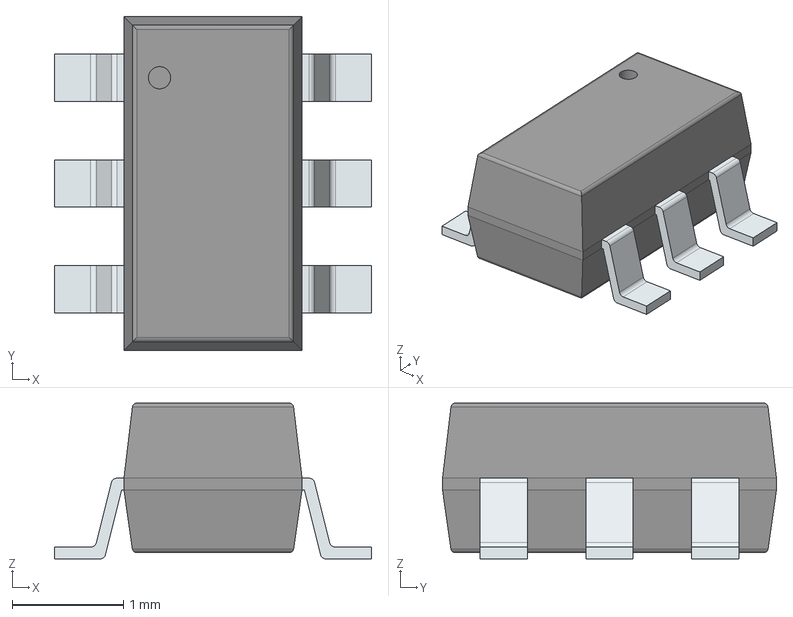
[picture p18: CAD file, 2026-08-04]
Fluo-Led/Fluo-Led/Importations/AL5801W6-7/3D/AL5801W6-7.stp
2.85 x 3.00 x 1.40 mm
PinsArrayLR

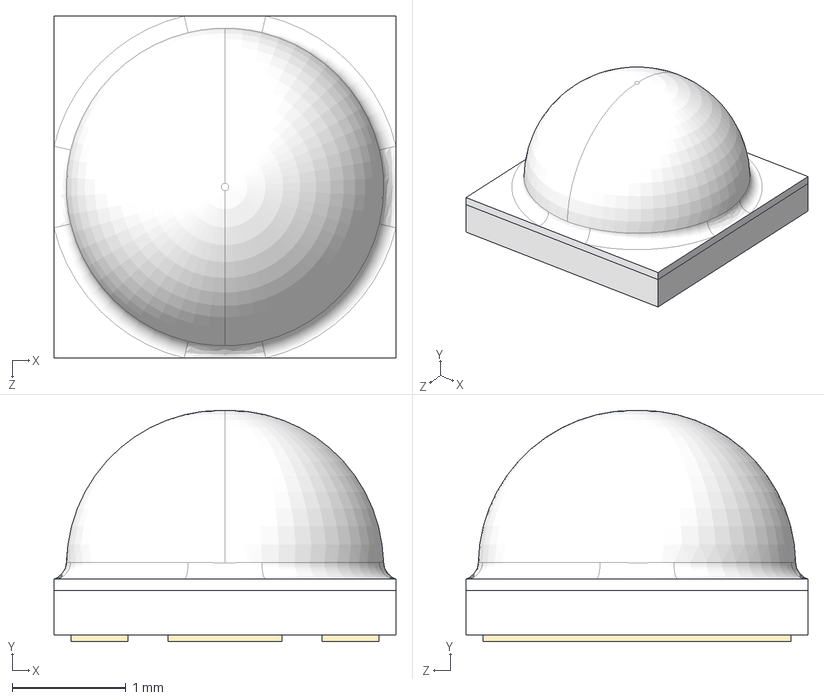
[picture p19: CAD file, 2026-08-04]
Fluo-Led/Fluo-Led/Importations/LV_CRBP.01-KXLY-AD-Q525-350-R18/3D/LV_CRBP.01-KXLY-AD-Q525-350-R18.stp
3.00 x 2.03 x 3.00 mm

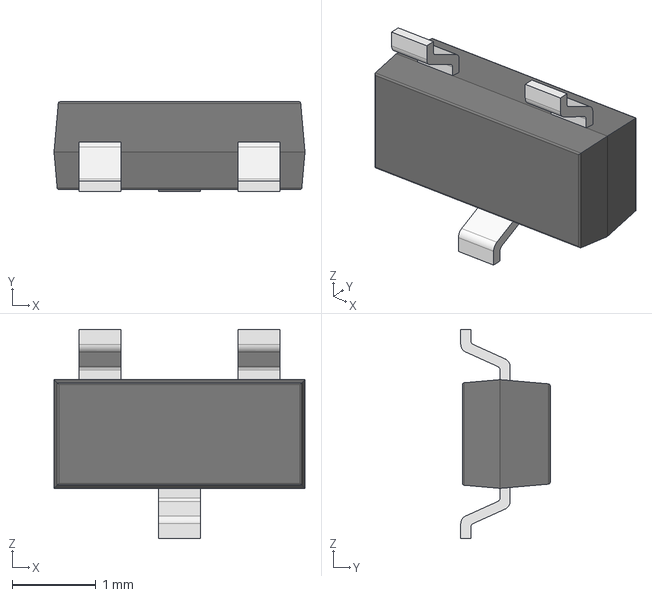
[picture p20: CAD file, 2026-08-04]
Microscope_STAR_D_PCB/LIB_SI2302B-TP/SI2302B-TP/SI2302B-TP.stp
3.00 x 1.07 x 2.50 mm
��1
��2

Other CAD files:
star-d_power-main/LD15P33E4GX00LF/LD15P33E4GX00LF.step
star-d_power-main/LD15S33E4GV00LF/LD15S33E4GV00LF.step
5V_board/0436500215.stp
5V_board/0532530470.stp
5V_board/5V_Board.step
AUTRE/CM5_MINIMA_REV2-main/CM5_MINIMA_REV2-main/3d_lib/3x4x2 tact button.step
AUTRE/CM5_MINIMA_REV2-main/CM5_MINIMA_REV2-main/3d_lib/BM4B-SRSS-TB.step
AUTRE/CM5_MINIMA_REV2-main/CM5_MINIMA_REV2-main/3d_lib/M.2-B.step
AUTRE/CM5_MINIMA_REV2-main/CM5_MINIMA_REV2-main/3d_lib/RAK3172--3DModel-STEP-100311.STEP
AUTRE/CM5_MINIMA_REV2-main/CM5_MINIMA_REV2-main/3d_lib/SHTC3-TR-10KS.stp
AUTRE/CM5_MINIMA_REV2-main/CM5_MINIMA_REV2-main/3d_lib/WE-RJ45LAN-7498111120AR (rev1).stp
AUTRE/Sans_heater_VFINAL_PCB_Rexus/importations/ISL83491IBZ-T/ISL83491IBZ-T.stp
BME280_External/BME280_External/0532530670.stp
Microscope_STAR_D_PCB/0436500312.SLDPRT
Microscope_STAR_D_PCB/0436500312.stp
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

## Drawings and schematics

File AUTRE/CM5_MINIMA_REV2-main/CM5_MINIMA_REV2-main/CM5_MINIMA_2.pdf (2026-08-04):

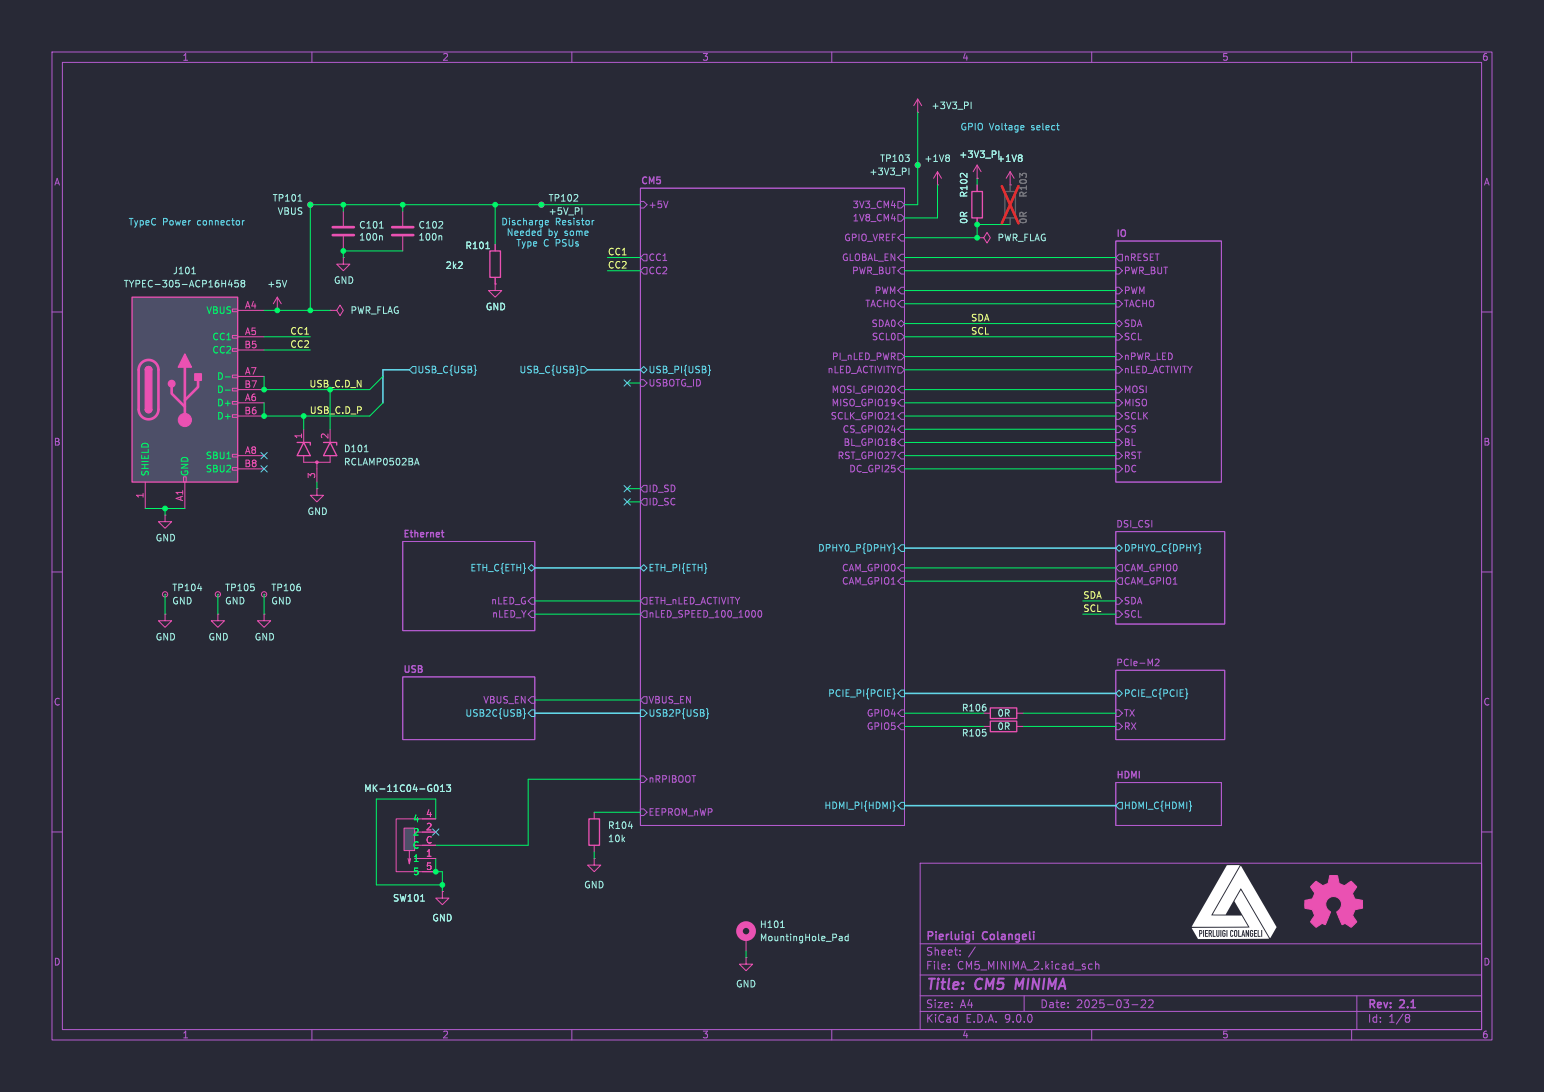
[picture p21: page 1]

PCIE_C{PCIE} PCIe-M2 HDMI_C{HDMI} HDMI USB_PI{USB} USBOTG_ID

SCL SDA DPHY0_C{DPHY} CAM_GPIO0 CAM_GPIO1 DSI_CSI ETH_C{ETH} nLED_Y

File: CM5_MINIMA_2.kicad_sch Sheet: / Pierluigi Colangeli

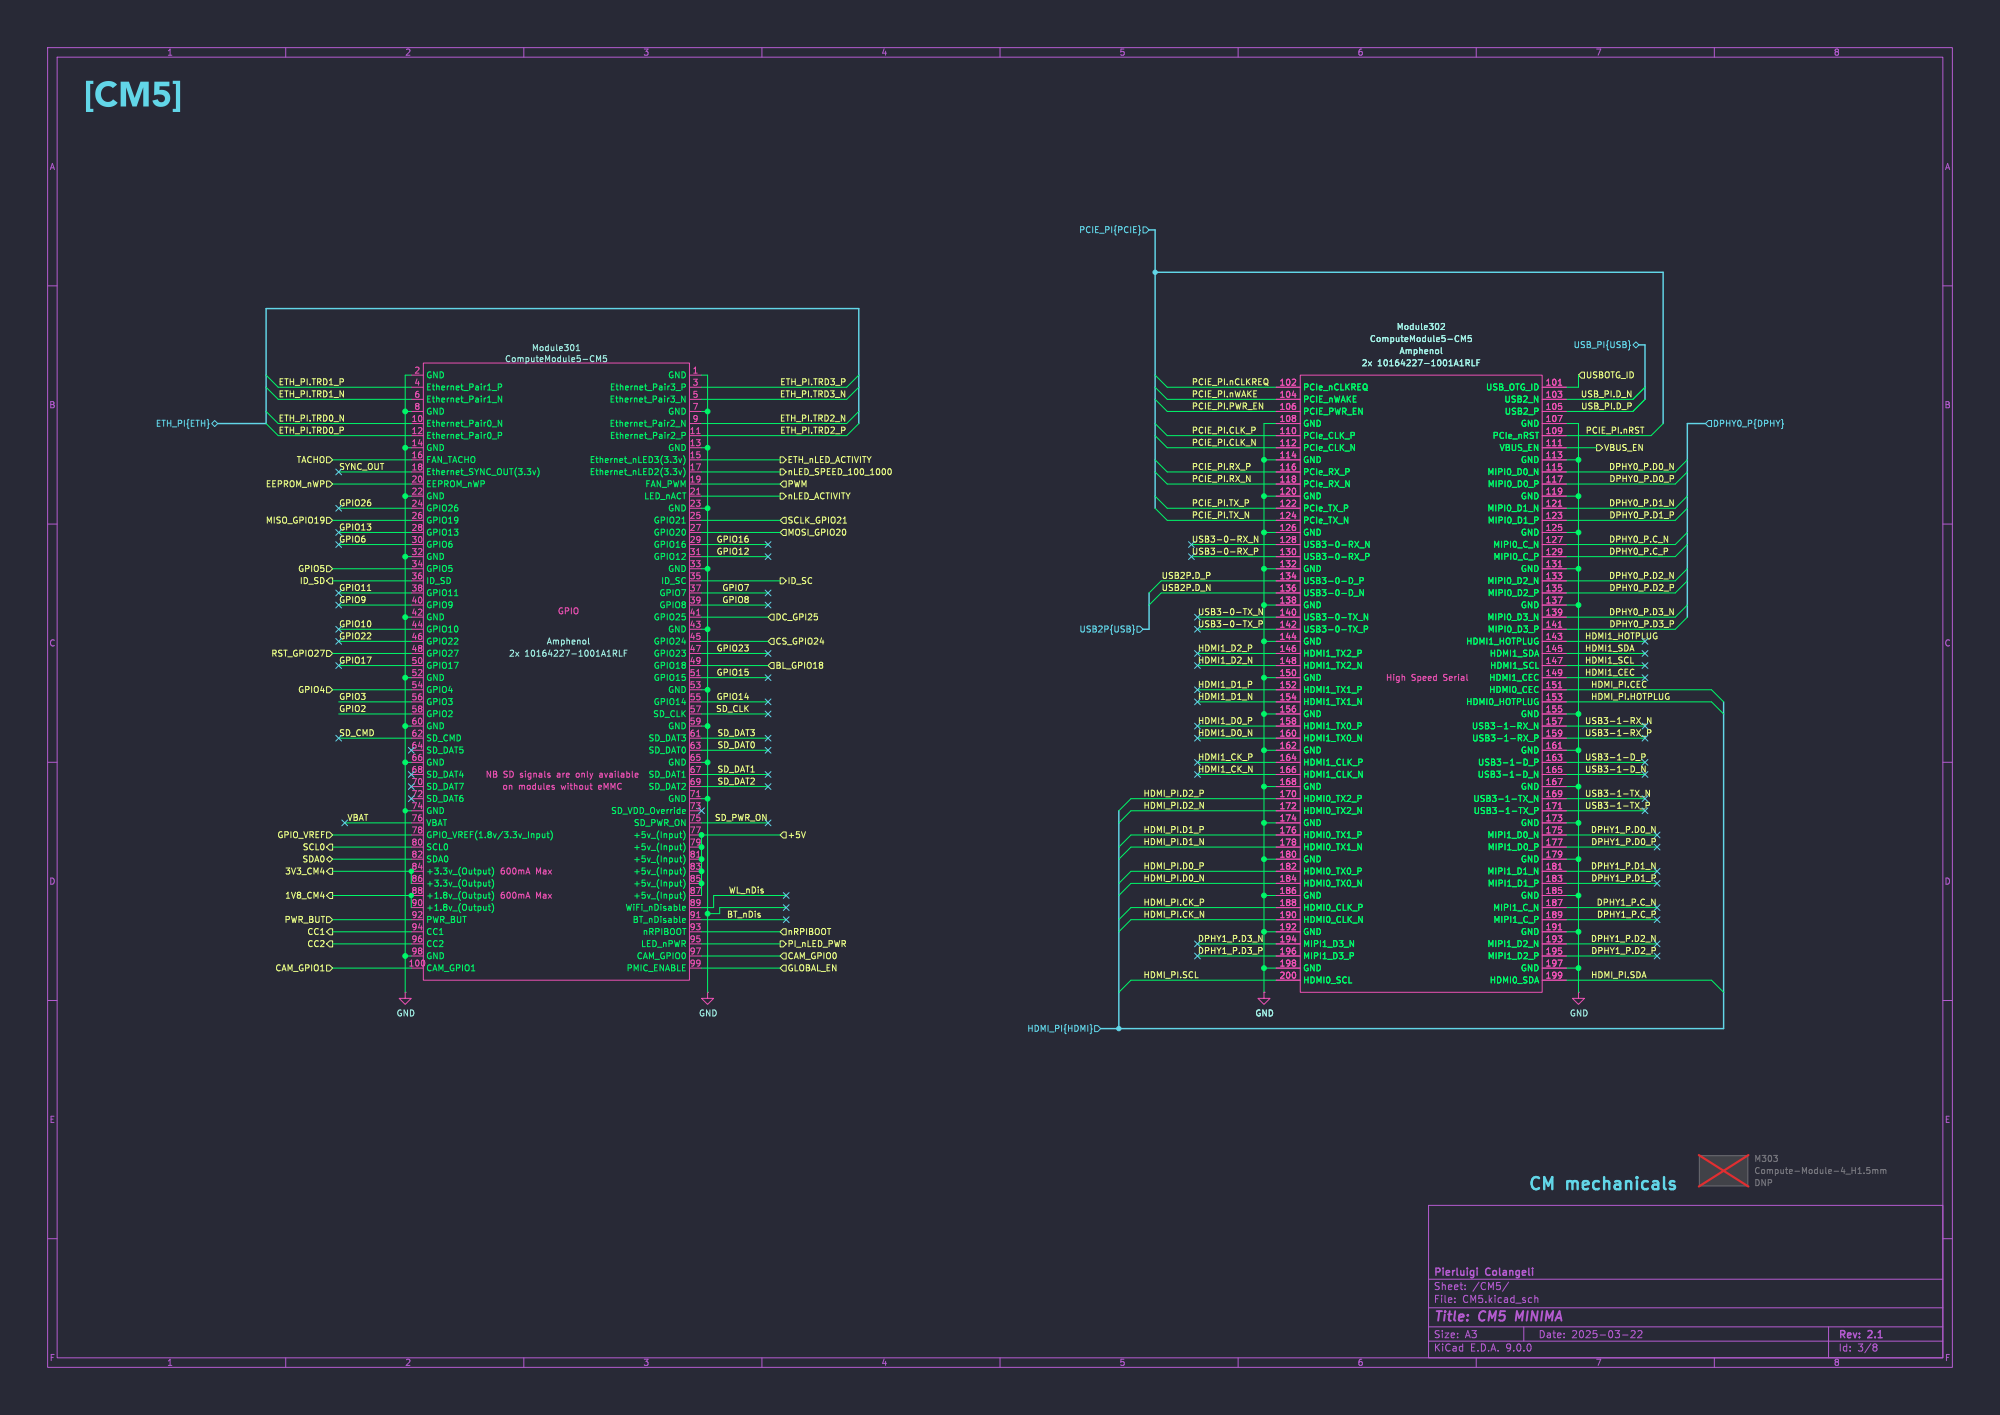
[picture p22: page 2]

GND 2 Ethernet_Pair1_P 4 Ethernet_Pair1_N 6 GND 8 Ethernet_Pair0_N 10 Ethernet_Pair0_P 12 GND 14 FAN_TACHO 16 Ethernet_SYNC_OUT(3.3v) 18 EEPROM_nWP 20 GND 22 GPIO26 24 GPIO19 26 GPIO13 28 GPIO6 30 GND 32 GPIO5 34
ID_SD 36 GPIO11 38 GPIO9 40 GND 42 GPIO10 44 GPIO22 46 GPIO27 48 GPIO17 50 GND 52 GPIO4 54 GPIO3 56 GPIO2 58 GND 60 SD_CMD 62 SD_DAT5 64 GND 66 SD_DAT4 68 SD_DAT7 70 SD_DAT6 72 GND 74 VBAT 76 GPIO_VREF(1.8v/3.3v_Input) 78 SCL0 80 SDA0 82 +3.3v_(Output) 84 +3.3v_(Output) 86 +1.8v_(Output) 88 +1.8v_(Output) 90 PWR_BUT 92 CC1 94 CC2 96 GND 98 CAM_GPIO1 100

on modules without eMMC GPIO

600mA Max 600mA Max NB SD signals are only available

File: CM5.kicad_sch Sheet: /CM5/ Pierluigi Colangeli

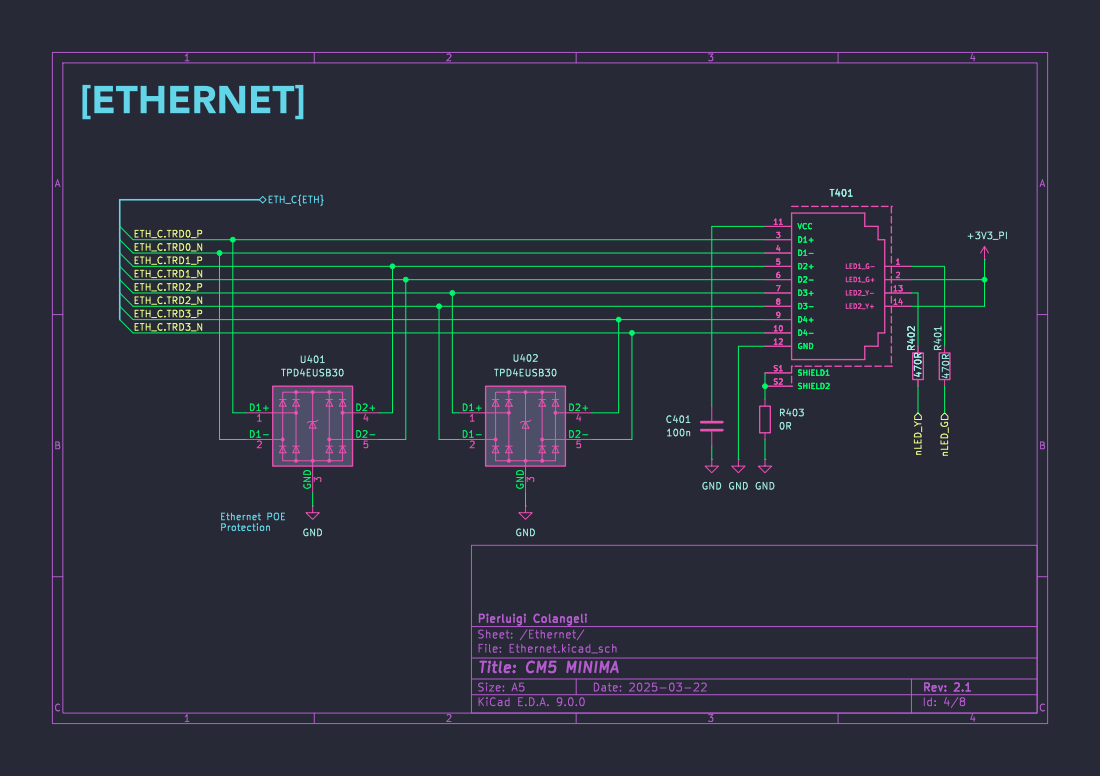
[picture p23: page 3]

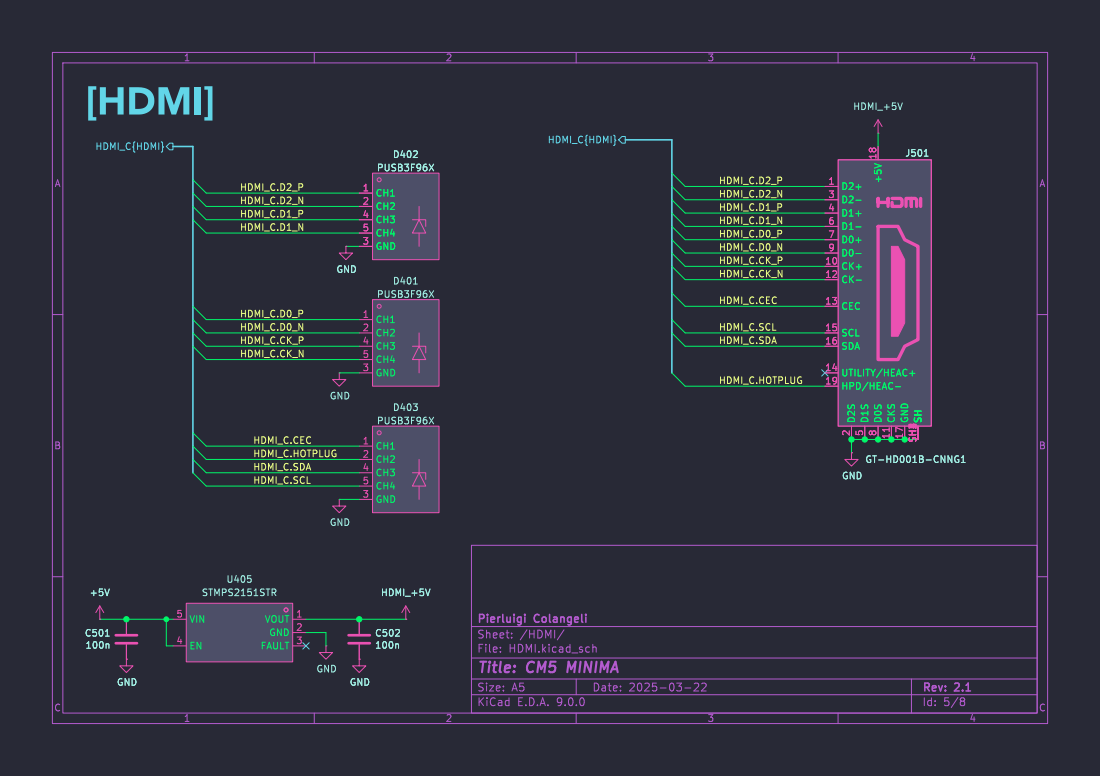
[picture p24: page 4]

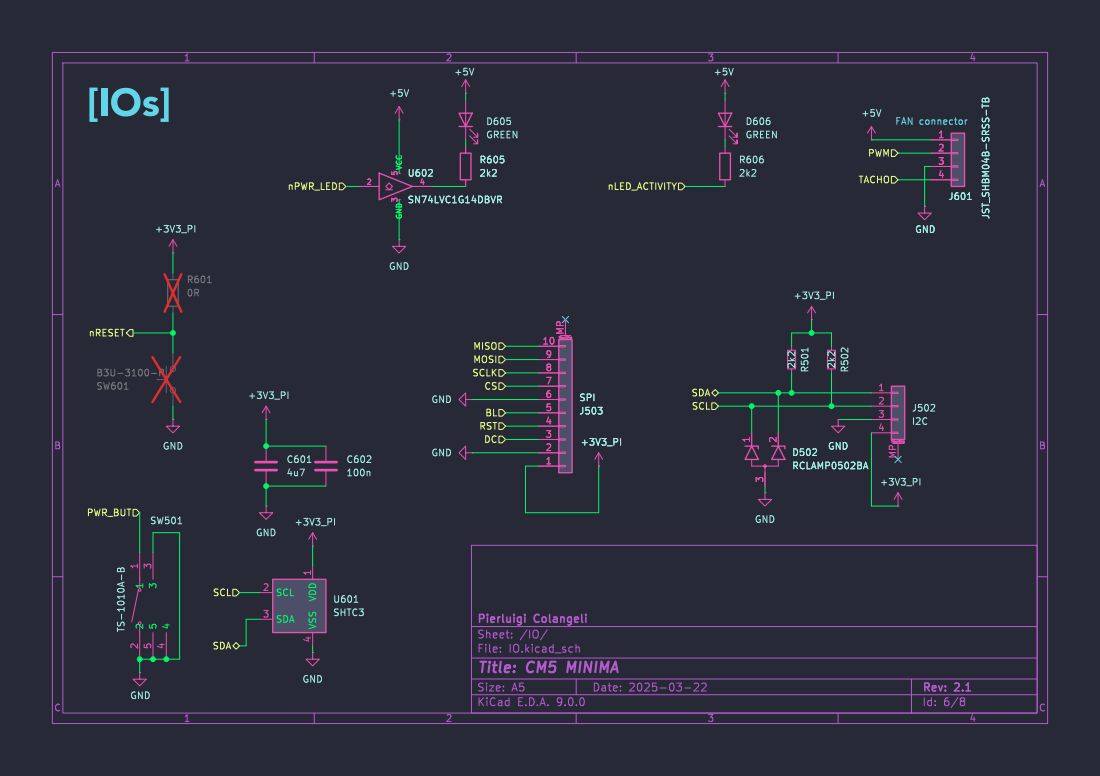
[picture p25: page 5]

2 | Mounting 1

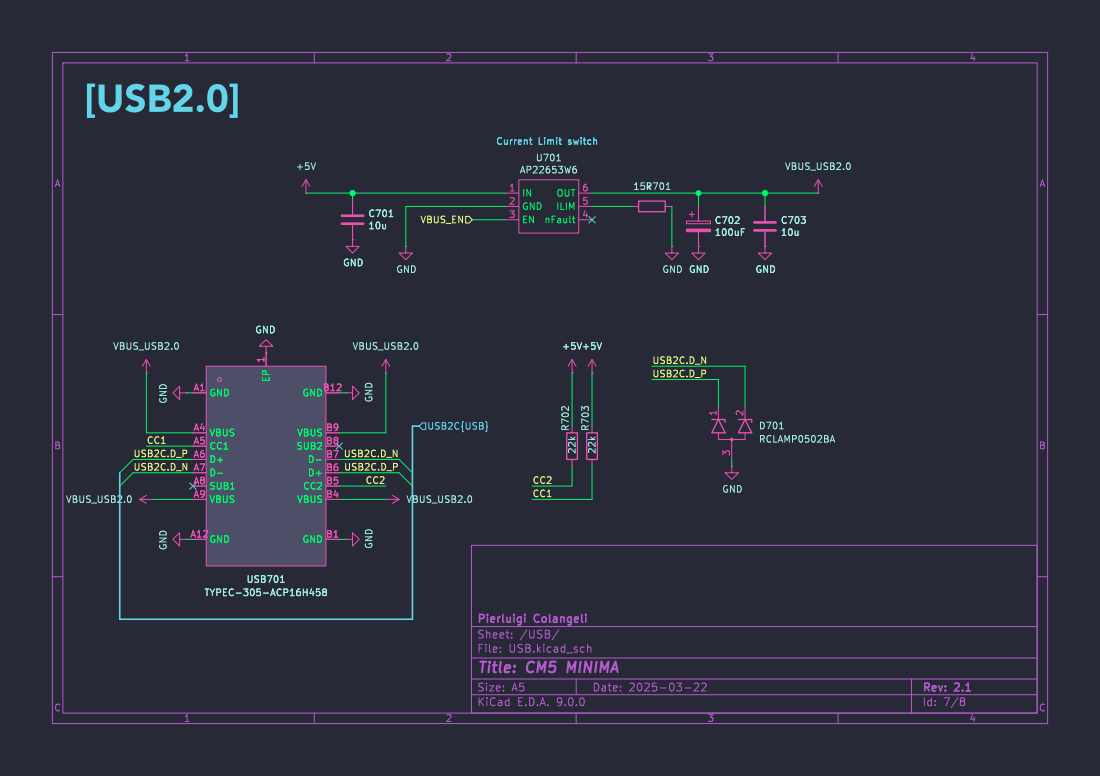
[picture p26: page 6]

File: USB.kicad_sch Sheet: /USB/ Pierluigi Colangeli C701
USB2C{USB} VBUS_EN
10uGND

1 GNDB12 VBUS B9 SUB2 B8 D- B7 D+ B6 CC2 B5 VBUS B4 GND B1 GND

1 GNDB12 VBUS B9 SUB2 B8 D- B7 D+ B6 CC2 B5 VBUS B4 GND B1 USB701 TYPEC-305-ACP16H458

2 D701 RCLAMP0502BA GND GND GND GND

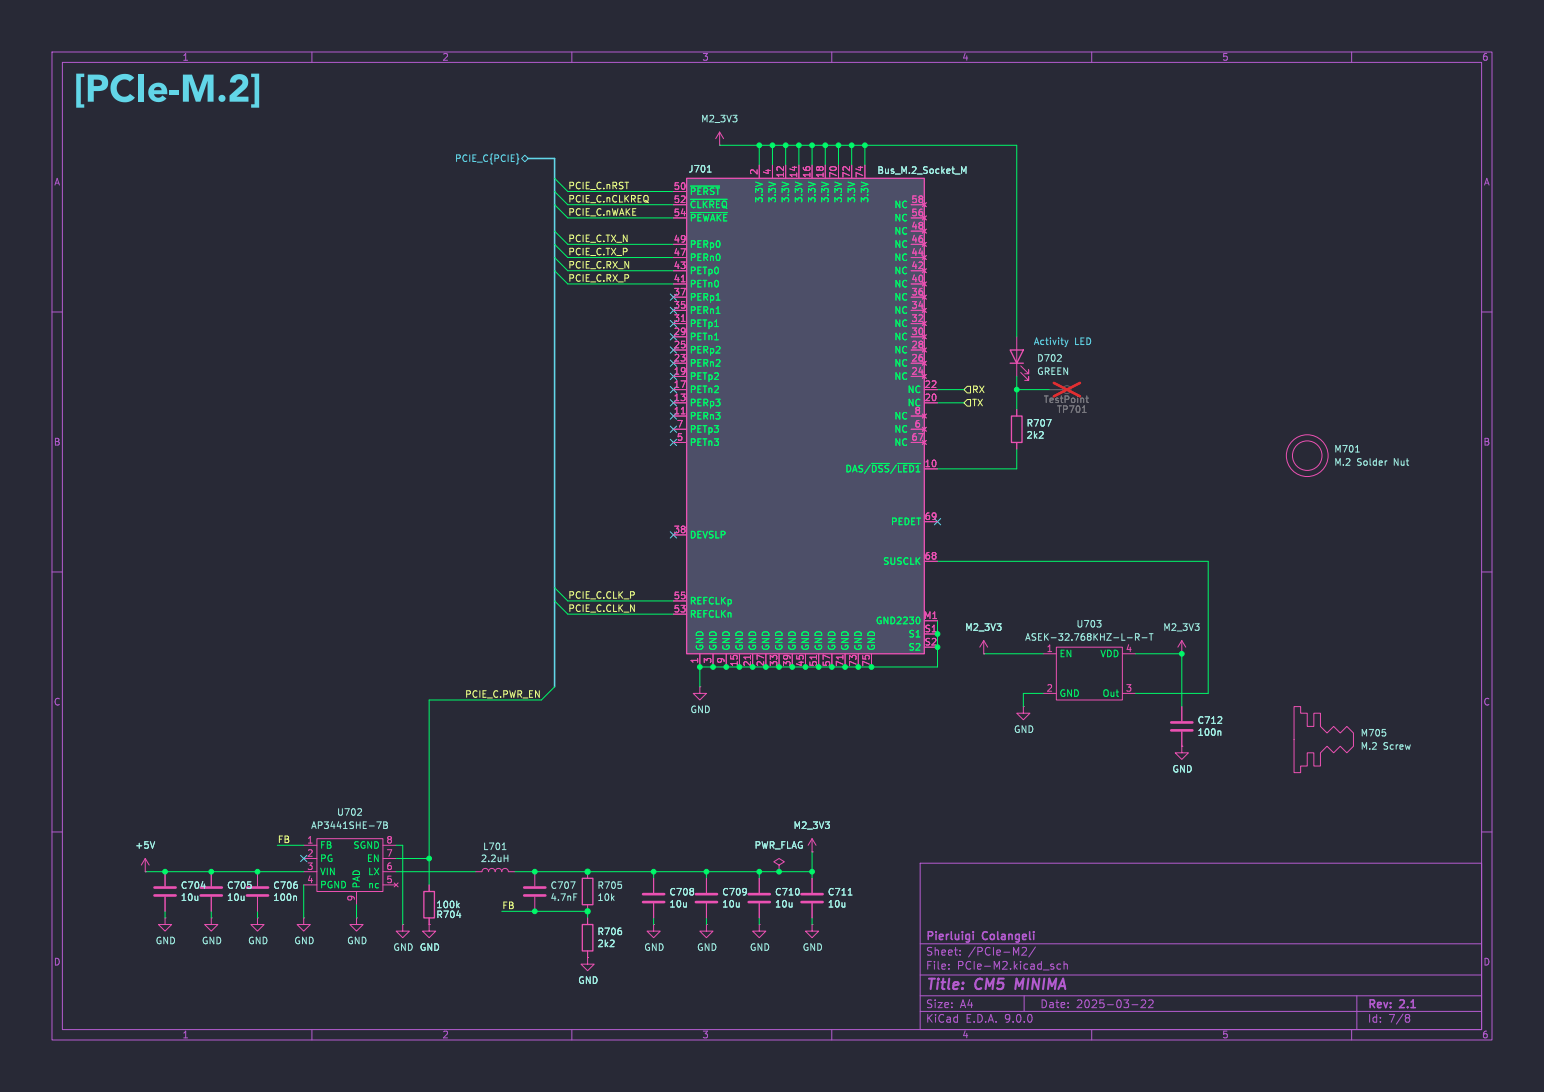
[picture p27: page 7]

4 GND 33 3.3V 12 GND 39 3.3V 14 GND 45 3.3V 16 GND 51 3.3V 18 GND 57 3.3V 70 GND 71 3.3V 72 GND 73 3.3V 74 GND 75 NC 58 NC 56 NC 48 NC 46 NC 44 NC 42 NC 40 NC 36 NC 34 NC 32 NC 30 NC 28 NC 26 NC 24 NC 8 NC 6 NC 67 NC 22 NC 20 DAS/~{DSS}/~{LED1} 10 PEDET 69 SUSCLK 68 GND2230 M1 S1 S1 S2 S2 C704

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

File: PCIe-M2.kicad_sch Sheet: /PCIe-M2/ Pierluigi Colangeli GND

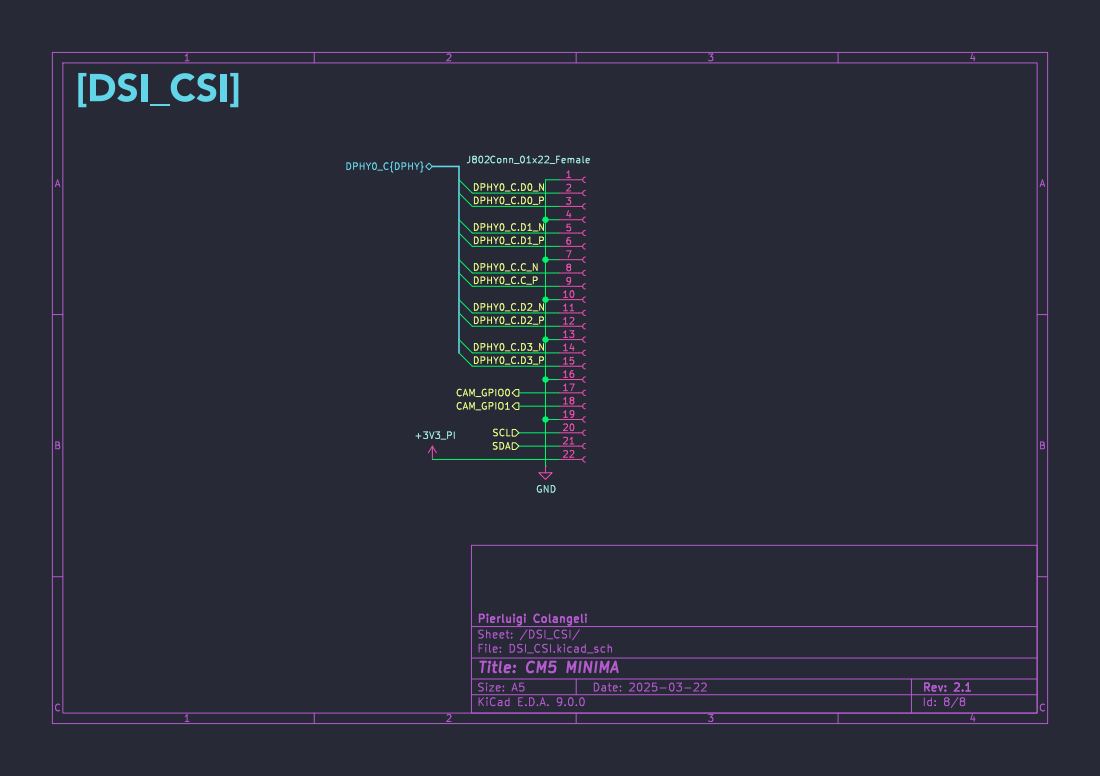
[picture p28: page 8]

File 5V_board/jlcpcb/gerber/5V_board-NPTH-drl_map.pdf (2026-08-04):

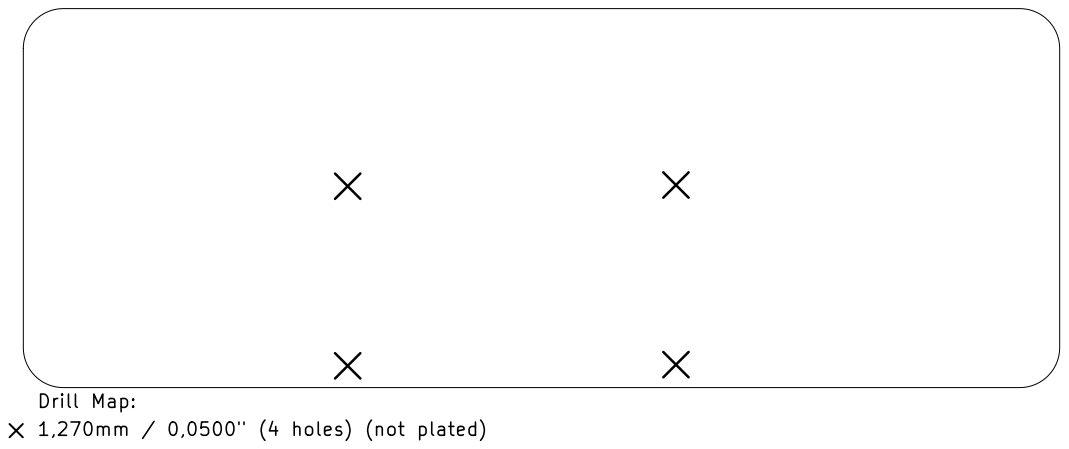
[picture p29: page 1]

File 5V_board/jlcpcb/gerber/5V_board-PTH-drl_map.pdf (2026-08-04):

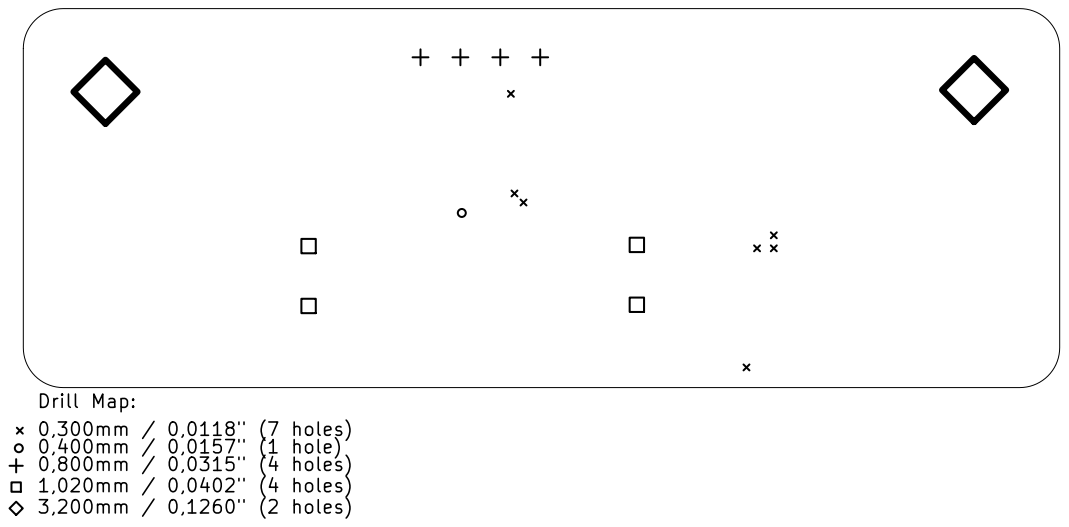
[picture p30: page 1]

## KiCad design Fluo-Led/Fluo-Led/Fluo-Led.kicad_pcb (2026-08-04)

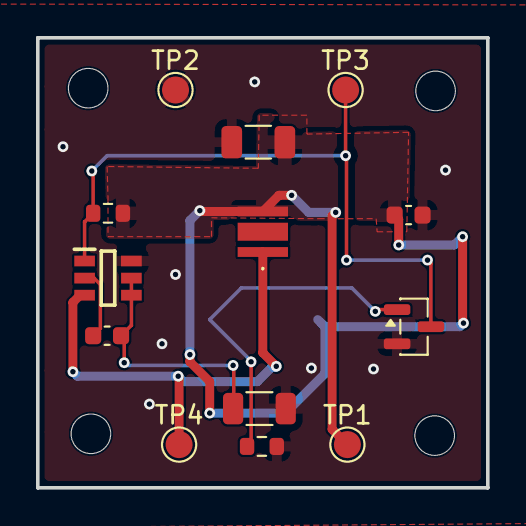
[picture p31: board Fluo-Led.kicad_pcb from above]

Board: 2 copper layers, 25.0 x 25.0 mm, 18 parts (1 on the bottom side), 7 nets.

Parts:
C1: 100nF 0603; C_0603_1608Metric
C2: 10uF 1206; C_1206_3216Metric
C3: 1 nF 0603; C_0603_1608Metric
H1, H2, H3, H4: MountingHole; MountingHole_2.2mm_M2
IC1: AL5801W6-7; SOT95P285X140-6N
J1: Conn_01x03; Molex_Micro-Fit_3.0_43650-0312_1x03-1MP_P3.00mm_Horizontal
LED1: LV_CRBP.01-KXLY-AD-Q525-350-R18; LVCRBP01KXLYADQ525350R18
Q1: 2N7002; SOT-23
R1: 4.02R 1206; R_1206_3216Metric
R2: 12.4k 0603; R_0603_1608Metric
R3: 100k 0603; R_0603_1608Metric
TP1, TP2, TP3, TP4: TestPoint; TestPoint_Pad_D1.5mm

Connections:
+5V: C1.1, C2.1, J1.1, LED1.2 (A), R2.1, TP1.1 (1_1)
BIAS: IC1.1 (BIAS), Q1.3 (D), R2.2, TP3.1 (1_1)
GND: C1.2, C2.2, IC1.6 (GND), J1.2, Q1.2 (S), R1.2, R3.1, TP2.1 (1_1)
unnamed: C3.1, IC1.4 (REXT), IC1.5 (COMP), R1.1
unnamed: C3.2, IC1.2 (FB)
unnamed: IC1.3 (OUT), LED1.1 (K), TP4.1 (1_1)
PWM_CTRL: J1.3, Q1.1 (G), R3.2

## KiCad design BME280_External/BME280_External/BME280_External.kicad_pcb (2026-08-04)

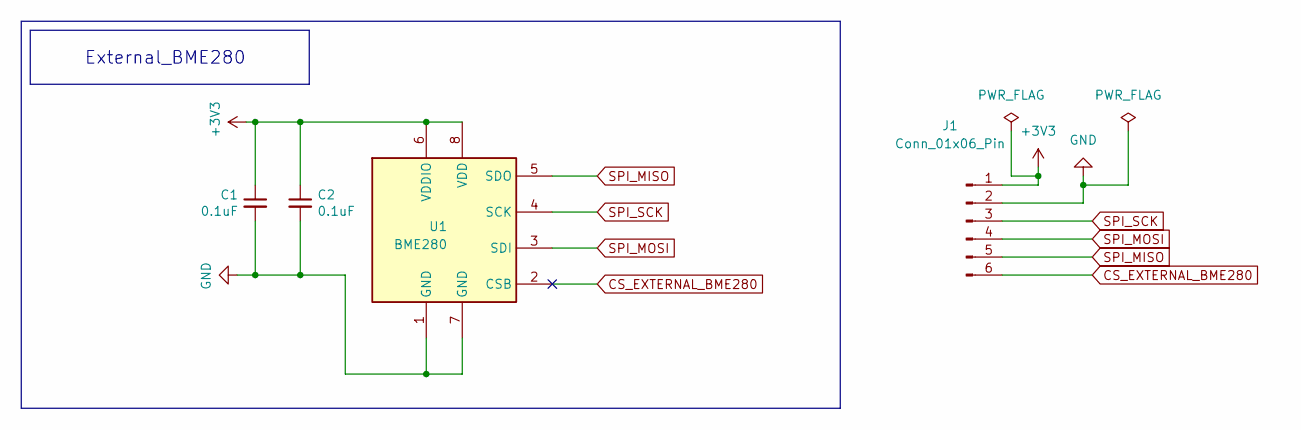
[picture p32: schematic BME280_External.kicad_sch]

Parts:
C1, C2: 0.1uF; C_0402_1005Metric
J1: Conn_01x06_Pin; Molex_Micro-Fit_3.0_43650-0615_1x06_P3.00mm_Vertical
U1: BME280; Bosch_LGA-8_2.5x2.5mm_P0.65mm_ClockwisePinNumbering

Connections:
+3V3: C1.1, C2.1, J1.1, U1.6 (VDDIO), U1.8 (VDD)
CS_EXTERNAL_BME280: J1.6, U1.2 (CSB)
GND: C1.2, C2.2, J1.2, U1.1 (GND), U1.7 (GND)
SPI_MISO: J1.5, U1.5 (SDO)
SPI_MOSI: J1.4, U1.3 (SDI)
SPI_SCK: J1.3, U1.4 (SCK)

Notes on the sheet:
External_BME280

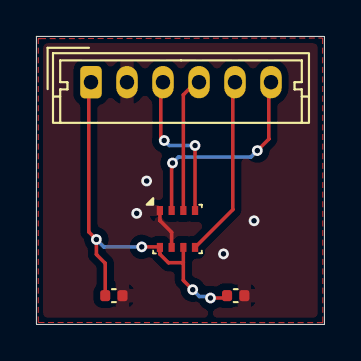
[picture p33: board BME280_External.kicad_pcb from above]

Board: 2 copper layers, 16.0 x 16.0 mm, 4 parts (0 on the bottom side), 6 nets.

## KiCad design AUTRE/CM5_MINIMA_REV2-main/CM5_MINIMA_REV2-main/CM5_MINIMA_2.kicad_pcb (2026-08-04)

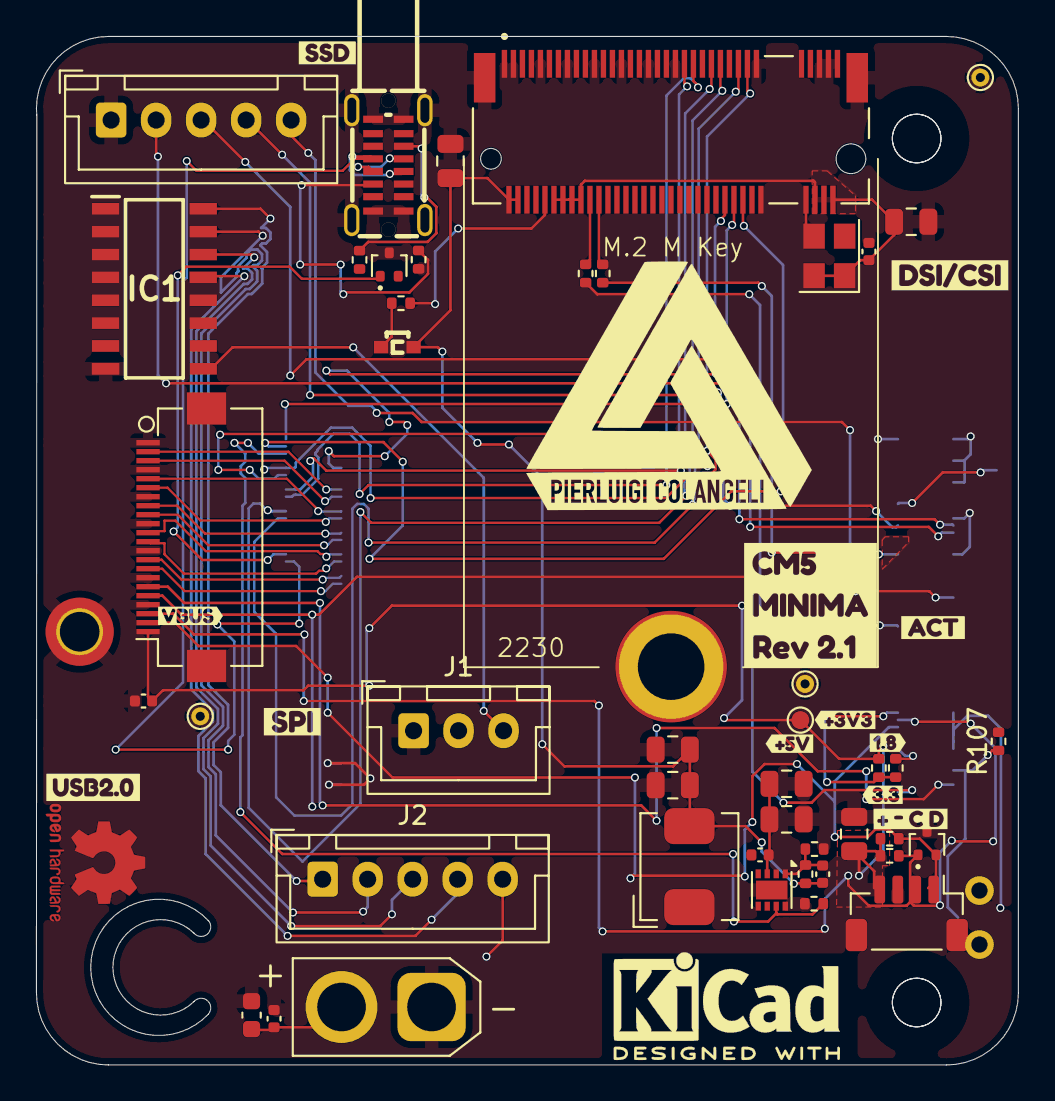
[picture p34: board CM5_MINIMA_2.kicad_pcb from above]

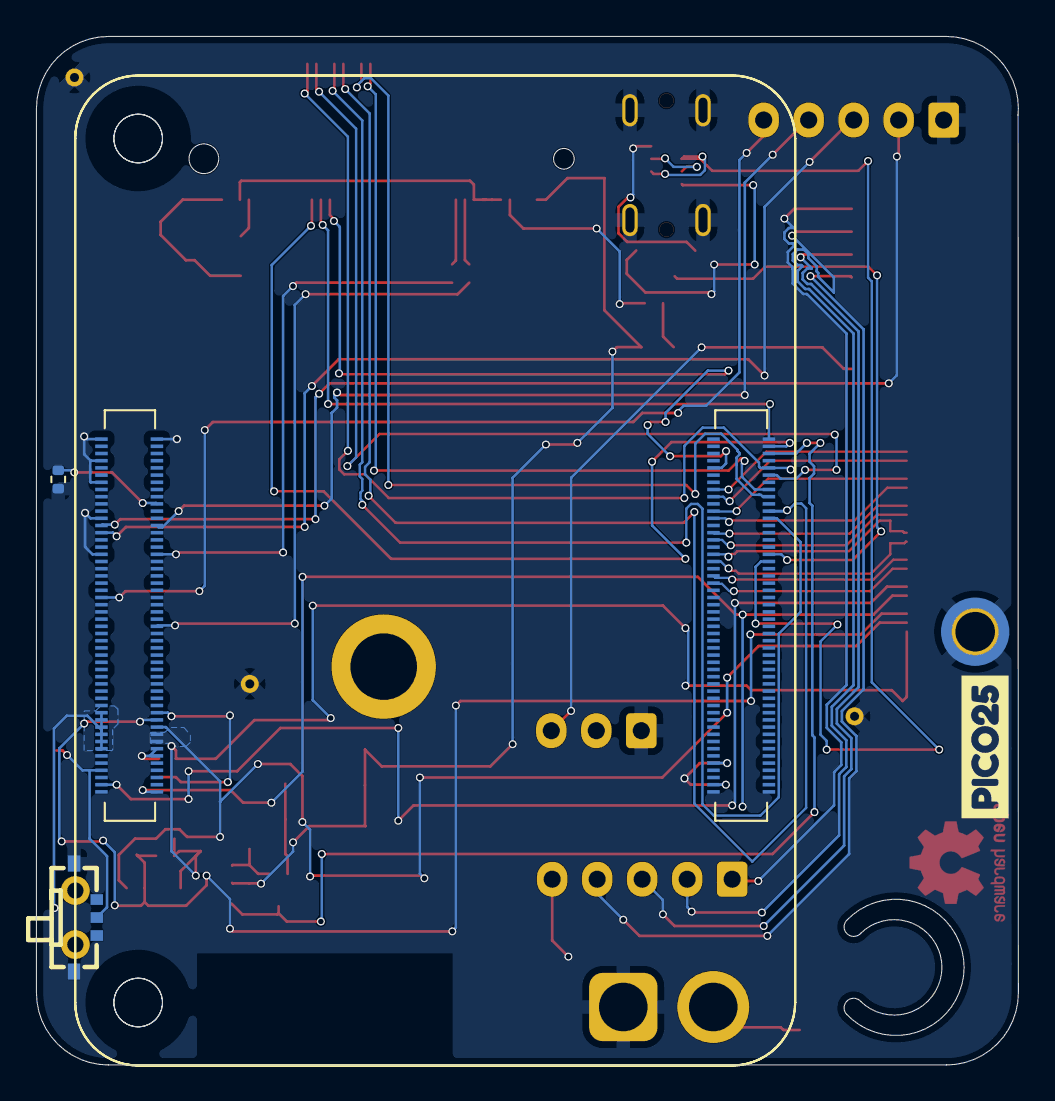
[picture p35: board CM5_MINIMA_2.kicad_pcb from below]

Board: 4 copper layers, 54.6 x 57.1 mm, 64 parts (5 on the bottom side), 58 nets.

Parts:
C31: 10uF 0603; C_0603_1608Metric
C33: 100nF 0402; C_0402_1005Metric
C601: 4u7; C_0805_2012Metric
C602, C706, C712: 100n; C_0402_1005Metric
C704, C705, C708, C709, C710, C711: 10u; C_0805_2012Metric
C707: 4.7nF; C_0402_1005Metric
D502, D701: RCLAMP0502BA; SOT-416
D702: GREEN; LED-SMD_L1.7-W0.6-RD
H101: MountingHole_Pad; MountingHole_2.2mm_M2_DIN965_Pad_TopBottom
IC1: ULN2003ADR; SOIC127P600X175-16N
J1: Conn_01x03; JST_XH_B3B-XH-A_1x03_P2.50mm_Vertical
J2, J3: Conn_01x05; JST_XH_B5B-XH-A_1x05_P2.50mm_Vertical
J13: Conn_01x02_Pin; AMASS_XT30U-F_1x02_P5.0mm_Vertical
J502: I2C; JST_SH_BM04B-SRSS-TB_1x04-1MP_P1.00mm_Vertical
J701: Bus_M.2_Socket_M; M.2 M Key socket 2230
J802: Conn_01x22_Female; Hirose_FH12-22S-0.5SH_1x22-1MP_P0.50mm_Horizontal
L701: 2.2uH; L_Bourns_SRP5030CC
M701: M.2 Solder Nut; MountingHole_3.78mm_M2_Pad_TopOnly
Module301: ComputeModule5-CM5; Raspberry-Pi-5-Compute-Module_GPIO
Module302: ComputeModule5-CM5; Raspberry-Pi-5-Compute-Module_HSS
R102, R103, R105, R106: 0R; R_0402_1005Metric
R104, R107, R705: 10k; R_0402_1005Metric
R501, R502, R706, R707: 2k2; R_0402_1005Metric
R702, R703: 5.1k; R_0402_1005Metric
R704: 100k; R_0402_1005Metric
SW101: MK-11C04-G013; SW-SMD_MK-11C04-G013
TP103: +3V3_PI; TestPoint_Pad_D1.0mm
TP104, TP105, TP106: GND; TestPoint_THTPad_D1.0mm_Drill0.5mm
U702: AP3441SHE-7B; DFN-8-1EP_2x2mm_P0.5mm_EP1.05x1.75mm
U703: ASEK-32.768KHZ-L-R-T; Crystal_SMD_3225-4Pin_3.2x2.5mm
USB701: TYPEC-305-ACP16H458; USB-C-SMD_TYPEC-305-ACP16H458
kibuzzard-675EDCA4: G***; kibuzzard-675EDCA4
kibuzzard-679BB153: G***; kibuzzard-679BB153
kibuzzard-6772DA33: G***; kibuzzard-6772DA33
kibuzzard-6773B9B9: G***; kibuzzard-6773B9B9
kibuzzard-6773B9CA: G***; kibuzzard-6773B9CA
kibuzzard-6773BA43: G***; kibuzzard-6773BA43
kibuzzard-6773BA89: G***; kibuzzard-6773BA89
kibuzzard-6773C2D7: G***; kibuzzard-6773C2D7
kibuzzard-6773C222: G***; kibuzzard-6773C222
kibuzzard-6773C376: G***; kibuzzard-6773C376
kibuzzard-6773CC4D: G***; kibuzzard-6773CC4D
kibuzzard-6773CC39: G***; kibuzzard-6773CC39
kibuzzard-67758943: G***; kibuzzard-67758943

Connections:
+1V8: Module301.88 (+1.8v_(Output)), Module301.90 (+1.8v_(Output)), R103.1
+3V3_PI: C601.1, C602.1, J502.4, J802.22, Module301.84 (+3.3v_(Output)), Module301.86 (+3.3v_(Output)), R102.1, R501.1, R502.1, TP103.1 (1_1)
+5V: C704.1, C705.1, C706.1, U702.3 (VIN)
+5V_MAIN: C31.1, C33.1, IC1.9 (COM), J1.3, J2.5, J13.2, Module301.77 (+5v_(Input)), Module301.79 (+5v_(Input)), Module301.81 (+5v_(Input)), Module301.83 (+5v_(Input)), Module301.85 (+5v_(Input)), Module301.87 (+5v_(Input))
/CM5/CAM_GPIO0: J802.17, Module301.97 (CAM_GPIO0)
/CM5/CAM_GPIO1: J802.18, Module301.100 (CAM_GPIO1)
/CM5/DPHY0_P.C_N: J802.8, Module302.127 (MIPI0_C_N)
/CM5/DPHY0_P.C_P: J802.9, Module302.129 (MIPI0_C_P)
/CM5/DPHY0_P.D0_N: J802.2, Module302.115 (MIPI0_D0_N)
/CM5/DPHY0_P.D0_P: J802.3, Module302.117 (MIPI0_D0_P)
/CM5/DPHY0_P.D1_N: J802.5, Module302.121 (MIPI0_D1_N)
/CM5/DPHY0_P.D1_P: J802.6, Module302.123 (MIPI0_D1_P)
/CM5/DPHY0_P.D2_N: J802.11, Module302.133 (MIPI0_D2_N)
/CM5/DPHY0_P.D2_P: J802.12, Module302.135 (MIPI0_D2_P)
/CM5/DPHY0_P.D3_N: J802.14, Module302.139 (MIPI0_D3_N)
/CM5/DPHY0_P.D3_P: J802.15, Module302.141 (MIPI0_D3_P)
/CM5/EEPROM_nWP: Module301.20 (EEPROM_nWP), R104.2
/CM5/GPIO4: Module301.54 (GPIO4), R106.2
/CM5/GPIO5: Module301.34 (GPIO5), R105.2
/CM5/GPIO_VREF: Module301.78 (GPIO_VREF(1.8v/3.3v_Input)), R102.2, R103.2
/CM5/PCIE_PI.CLK_N: J701.53 (REFCLKn), Module302.112 (PCIe_CLK_N)
/CM5/PCIE_PI.CLK_P: J701.55 (REFCLKp), Module302.110 (PCIe_CLK_P)
/CM5/PCIE_PI.PWR_EN: Module302.106 (PCIE_PWR_EN), R704.1, U702.7 (EN)
/CM5/PCIE_PI.RX_N: J701.43 (PETp0), Module302.118 (PCIe_RX_N)
/CM5/PCIE_PI.RX_P: J701.41 (PETn0), Module302.116 (PCIe_RX_P)
/CM5/PCIE_PI.TX_N: J701.49 (PERp0), Module302.124 (PCIe_TX_N)
/CM5/PCIE_PI.TX_P: J701.47 (PERn0), Module302.122 (PCIe_TX_P)
/CM5/PCIE_PI.nCLKREQ: J701.52 (~CLKREQ), Module302.102 (PCIe_nCLKREQ)
/CM5/PCIE_PI.nRST: J701.50 (~PERST), Module302.109 (PCIe_nRST)
/CM5/PCIE_PI.nWAKE: J701.54 (~PEWAKE), Module302.104 (PCIE_nWAKE)
/CM5/USB2P.D_N: D701.2 (K2), Module302.136 (USB3-0-D_N), USB701.A7 (D-), USB701.B7 (D-)
/CM5/USB2P.D_P: D701.1 (K1), Module302.134 (USB3-0-D_P), USB701.A6 (D+), USB701.B6 (D+)
/CM5/nRPIBOOT: Module301.93 (nRPIBOOT), R107.1, SW101.C
/IO/COIL_A: IC1.16 (1C), J2.1
/IO/COIL_B: IC1.15 (2C), J2.2
/IO/COIL_C: IC1.14 (3C), J2.3
/IO/COIL_D: IC1.13 (4C), J2.4
/PCIe-M2/FB: C707.2, R705.2, R706.1, U702.1 (FB)
/PCIe-M2/RX: J701.22 (NC), R105.1
/PCIe-M2/TX: J701.20 (NC), R106.1
/SCL: D502.1 (K1), J502.2, J802.20, Module301.80 (SCL0), R502.2
/SDA: D502.2 (K2), J502.1, J802.21, Module301.82 (SDA0), R501.2
/USB/CC1: R703.1, USB701.A5 (CC1)
/USB/CC2: R702.1, USB701.B5 (CC2)
CS_RASP: J3.5, Module301.45 (GPIO24)
GND: C31.2, C33.2, C601.2, C602.2, C704.2, C705.2, C706.2, C708.2, C709.2, C710.2, C711.2, C712.2, D502.3 (A), D701.3 (A), H101.1 (1_1), IC1.8 (E), J1.1, J3.1, J13.1, J502.3, J701.1 (GND), J701.3 (GND), J701.9 (GND), J701.15 (GND), J701.21 (GND), J701.27 (GND), J701.33 (GND), J701.39 (GND), J701.45 (GND), J701.51 (GND), J701.57 (GND), J701.71 (GND), J701.73 (GND), J701.75 (GND), J701.S1, J701.S2, J802.1, J802.4, J802.7, J802.10, J802.13, J802.16, J802.19, Module301.1 (GND), Module301.2 (GND), Module301.7 (GND), Module301.8 (GND), Module301.13 (GND), Module301.14 (GND), Module301.22 (GND), Module301.23 (GND), Module301.32 (GND), Module301.33 (GND), Module301.42 (GND), Module301.43 (GND), Module301.52 (GND), Module301.53 (GND), Module301.59 (GND), Module301.60 (GND), Module301.65 (GND), Module301.66 (GND), Module301.71 (GND), Module301.74 (GND), Module301.98 (GND), Module302.107 (GND), Module302.108 (GND), Module302.113 (GND), Module302.114 (GND), Module302.119 (GND), Module302.120 (GND), Module302.125 (GND), Module302.126 (GND), Module302.131 (GND), Module302.132 (GND), Module302.137 (GND), Module302.138 (GND), Module302.144 (GND), Module302.150 (GND), Module302.155 (GND), Module302.156 (GND), Module302.161 (GND), Module302.162 (GND), Module302.167 (GND), Module302.168 (GND), Module302.173 (GND), Module302.174 (GND), Module302.179 (GND), Module302.180 (GND), Module302.185 (GND), Module302.186 (GND), Module302.191 (GND), Module302.192 (GND), Module302.197 (GND), Module302.198 (GND), R104.1, R702.2, R703.2, R704.2, R706.2, SW101.5, TP104.1 (1_1), TP105.1 (1_1), TP106.1 (1_1), U702.4 (PGND), U702.8 (SGND), U702.9 (PAD), U703.2 (GND), USB701.1 (EP), USB701.A1 (GND), USB701.A12 (GND), USB701.B1 (GND), USB701.B12 (GND)
M2_3V3: C707.1, C708.1, C709.1, C710.1, C711.1, C712.1, D702.2 (A), J701.2 (3.3V), J701.4 (3.3V), J701.12 (3.3V), J701.14 (3.3V), J701.16 (3.3V), J701.18 (3.3V), J701.70 (3.3V), J701.72 (3.3V), J701.74 (3.3V), L701.2, R705.1, U703.1 (EN), U703.4 (VDD)
unnamed: D702.1 (K), R707.1
unnamed: J701.10 (DAS/~DSS/~LED1), R707.2
unnamed: J701.68 (SUSCLK), U703.3 (Out)
unnamed: L701.1, U702.6 (LX)
RASP_CLK: J3.2, Module301.25 (GPIO21)
RASP_MISO: J3.4, Module301.26 (GPIO19)
RASP_MOSI: J3.3, Module301.27 (GPIO20)
STEP_IN1: IC1.1 (1B), Module301.29 (GPIO16)
STEP_IN2: IC1.2 (2B), Module301.31 (GPIO12)
STEP_IN3: IC1.3 (3B), Module301.37 (GPIO7)
STEP_IN4: IC1.4 (4B), Module301.39 (GPIO8)

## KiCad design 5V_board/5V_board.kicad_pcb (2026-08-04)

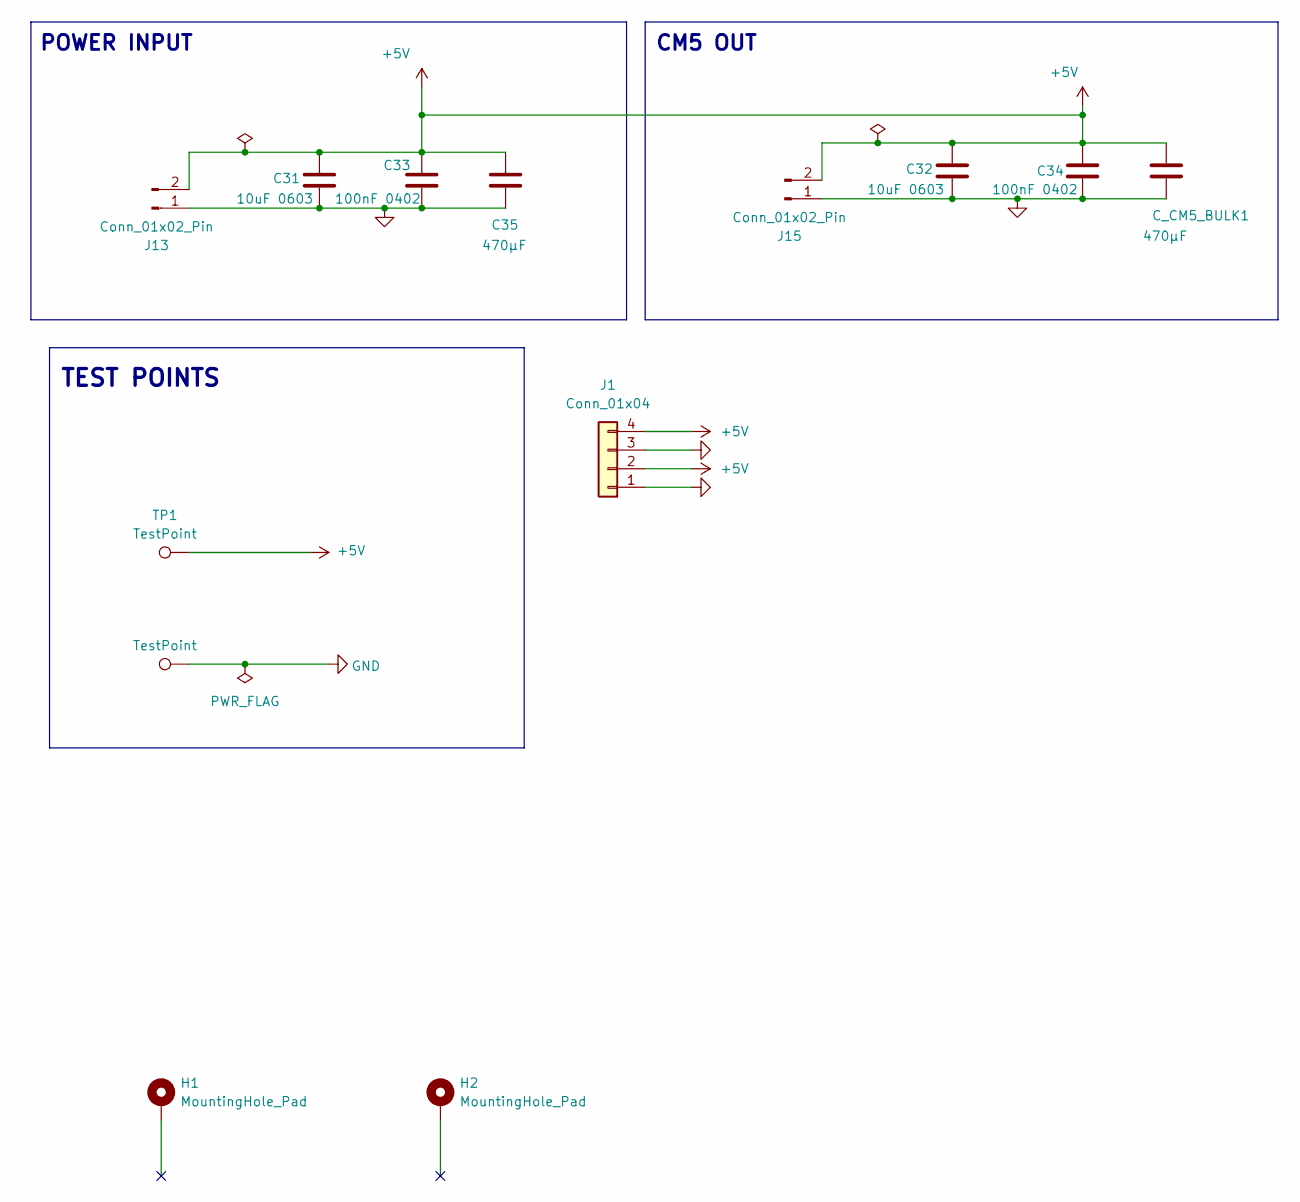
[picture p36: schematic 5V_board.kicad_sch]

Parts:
C31, C32: 10uF 0603; C_0603_1608Metric
C33, C34: 100nF 0402; C_0402_1005Metric
C35: 470µF; CP_Elec_6.3x7.7
C_CM5_BULK1: 470µF; CP_Elec_6.3x7.7
H1, H2: MountingHole_Pad; MountingHole_3.2mm_M3_Pad
J1: Conn_01x04; Molex_Micro-Latch_53253-0470_1x04_P2.00mm_Vertical
J13, J15: Conn_01x02_Pin; Molex_Micro-Fit_3.0_43650-0215_1x02_P3.00mm_Vertical
TP1, TP3: TestPoint; TestPoint_Pad_D1.5mm

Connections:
+5V: C31.1, C32.1, C33.1, C34.1, C35.1, C_CM5_BULK1.1, J1.2, J1.4, J13.2, J15.2, TP1.1 (1_1)
GND: C31.2, C32.2, C33.2, C34.2, C35.2, C_CM5_BULK1.2, J1.1, J1.3, J13.1, J15.1, TP3.1 (1_1)

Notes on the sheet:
TEST POINTS
POWER INPUT
CM5 OUT

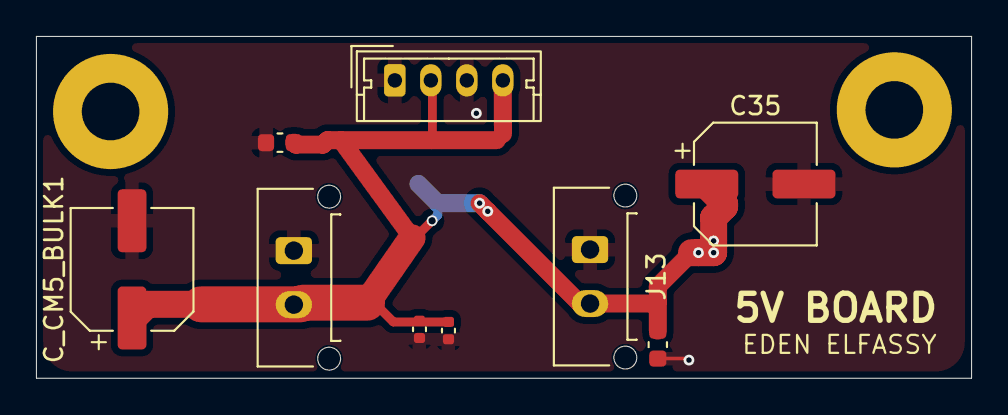
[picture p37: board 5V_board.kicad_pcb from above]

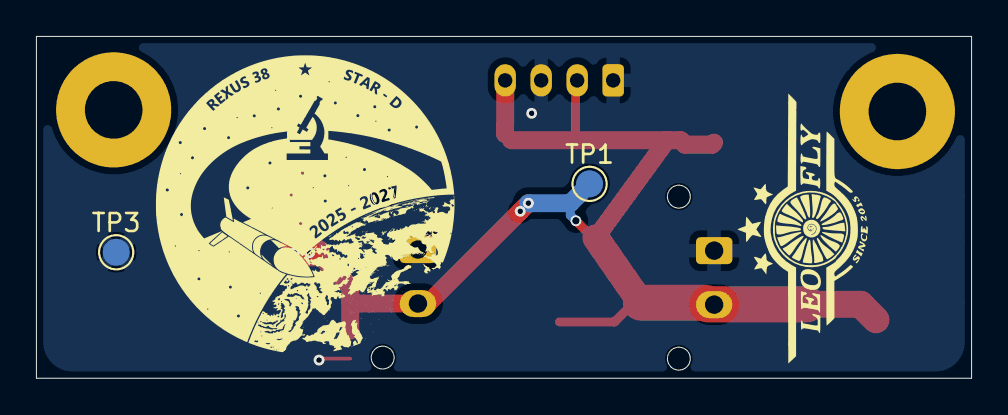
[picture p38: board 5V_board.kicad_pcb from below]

Board: 2 copper layers, 51.9 x 19.0 mm, 13 parts (2 on the bottom side), 2 nets.

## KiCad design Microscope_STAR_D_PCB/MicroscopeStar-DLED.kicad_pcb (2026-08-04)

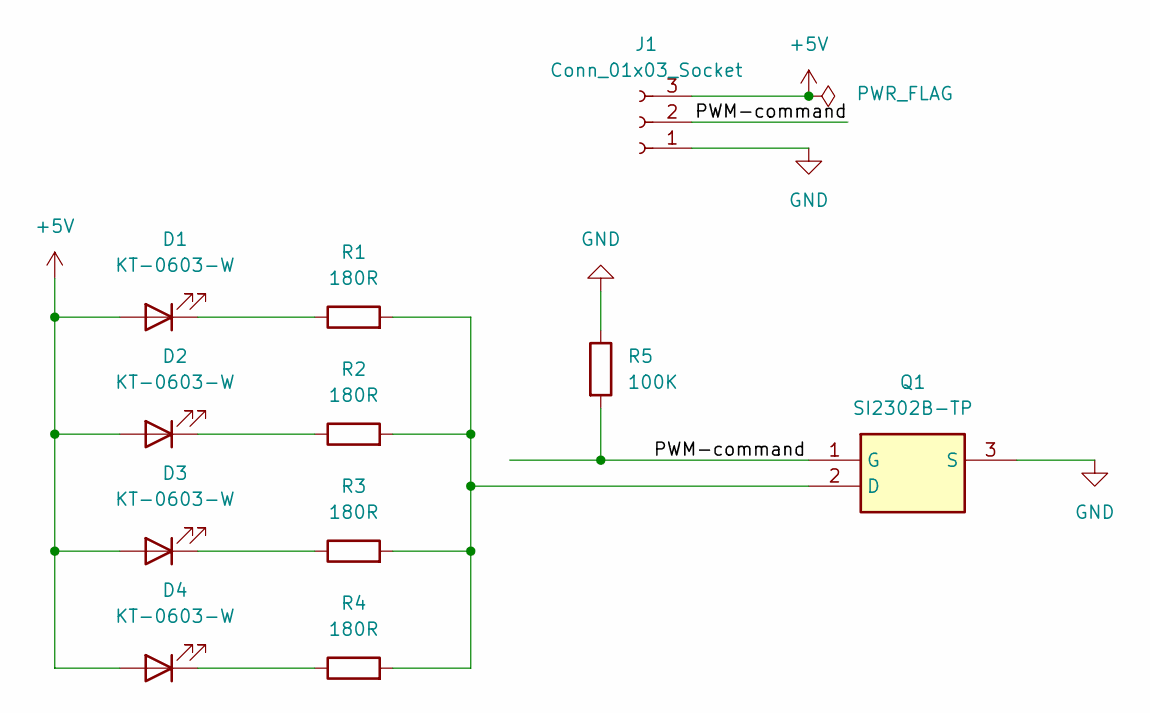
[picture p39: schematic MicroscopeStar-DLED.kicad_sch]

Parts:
D1, D2, D3, D4: KT-0603-W; LED_0603_1608Metric
J1: Conn_01x03_Socket; Molex_Micro-Fit_3.0_43650-0312_1x03-1MP_P3.00mm_Horizontal
Q1: SI2302B-TP; SOT95P237X125-3N; Manufacturer_Part_Number SI2302B-TP; Mouser Part Number 833-SI2302B-TP
R1, R2, R3, R4: 180R; R_0402_1005Metric
R5: 100K

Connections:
+5V: D1.2 (A), D2.2 (A), D3.2 (A), D4.2 (A), J1.3
/PWM-command: J1.2, Q1.1 (G), R5.2
GND: J1.1, Q1.3 (S), R5.1
unnamed: D1.1 (K), R1.1
unnamed: D2.1 (K), R2.1
unnamed: D3.1 (K), R3.1
unnamed: D4.1 (K), R4.1
unnamed: Q1.2 (D), R1.2, R2.2, R3.2, R4.2

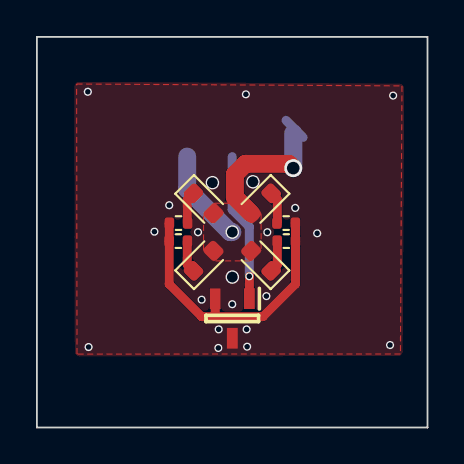
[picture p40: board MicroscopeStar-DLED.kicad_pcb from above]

Board: 2 copper layers, 21.7 x 21.7 mm, 10 parts (1 on the bottom side), 8 nets.

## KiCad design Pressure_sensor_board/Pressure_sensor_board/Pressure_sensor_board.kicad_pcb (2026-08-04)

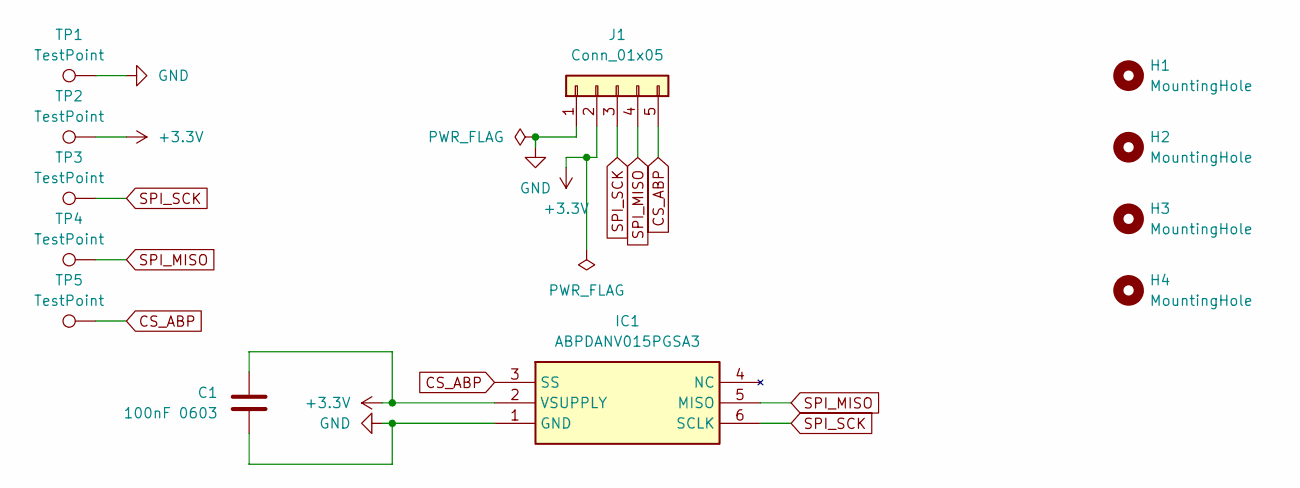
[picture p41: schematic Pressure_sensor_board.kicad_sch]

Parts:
C1: 100nF 0603; C_0603_1608Metric
H1, H2, H3, H4: MountingHole; MountingHole_2.2mm_M2
IC1: ABPDANV015PGSA3; Manufacturer_Part_Number ABPDANV015PGSA3; Mouser Part Number 785-ABPDANV015PGSA3
J1: Conn_01x05; Molex_Micro-Latch_53254-0570_1x05_P2.00mm_Horizontal
TP1, TP2, TP3, TP4, TP5: TestPoint; TestPoint_Pad_D1.5mm

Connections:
+3.3V: C1.2, IC1.2 (VSUPPLY), J1.2, TP2.1 (1_1)
CS_ABP: IC1.3 (SS), J1.5, TP5.1 (1_1)
GND: C1.1, IC1.1 (GND), J1.1, TP1.1 (1_1)
SPI_MISO: IC1.5 (MISO), J1.4, TP4.1 (1_1)
SPI_SCK: IC1.6 (SCLK), J1.3, TP3.1 (1_1)

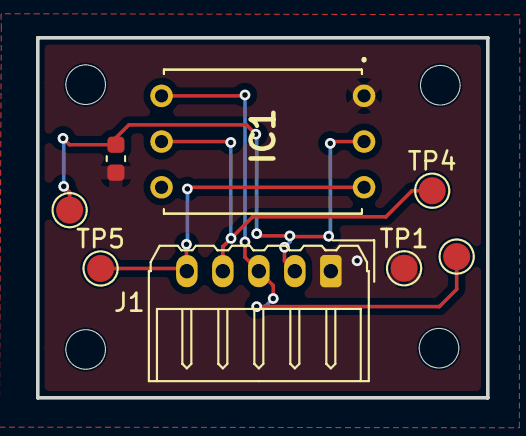
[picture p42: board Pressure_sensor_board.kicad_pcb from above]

Board: 2 copper layers, 25.0 x 20.0 mm, 12 parts (0 on the bottom side), 5 nets.

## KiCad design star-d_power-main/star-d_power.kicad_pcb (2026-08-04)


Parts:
C1_1, C1_2, C1_3, C1_4, C1_5, C1_6, C1_7, C1_8, C1_9, C1_10, C1_11, C1_12, C1_13, C1_14, C1_15, C1_16, C1_17, C1_18: 4.7uF; C_1206_3216Metric; Manufacturer_Part_Number GRM31CR71H475KA12L
C2_1, C2_2, C2_3: 8200pF; C_0603_1608Metric; Manufacturer_Part_Number VJ0603Y822KXAAC
C3_1, C3_2, C3_3: 4.7uF; C_0603_1608Metric; Manufacturer_Part_Number GRM188Z71A475ME15D
C4_1, C4_2, C4_3: 100nF; C_0603_1608Metric; Manufacturer_Part_Number C0603C104K3RAC7411
C5_1, C5_2, C5_3, C5_4, C5_5, C5_6: 47uF; C_1210_3225Metric; Manufacturer_Part_Number GRM32ER71A476KE15L
C5_7, C5_8, C5_9: 47uF; C_2220_5750Metric; Manufacturer_Part_Number CGA9N3X7R1E476M230KB
CD_1, CD_2: 100nF; C_0603_1608Metric; Manufacturer_Part_Number C0603C104K3RAC7411
CF1: 1uF; C_1206_3216Metric; Manufacturer_Part_Number C3216X7R1H105K160AB
CFT1, CFT2, CFT3, CFT4: C_Feedthrough; NFM18CC101R1C3D; Manufacturer_Part_Number NFM18CC221R1C3D
D1, D2, D3: LED; LED_0603_1608Metric; Manufacturer_Part_Number LTST-C191KFKT
FL1: Common Mode Choke 215uH; PA2754NL; Manufacturer_Part_Number PA2754NL
IC1, IC2, IC3: MAX17639AFN+; MAX17793AFN; Manufacturer_Part_Number MAX17639AFN+
J1: 3.3V connector; Molex_Micro-Fit_3.0_43650-0200_1x02_P3.00mm_Horizontal; Manufacturer_Part_Number 43650-0200
J2: 5V connector; Molex_Micro-Fit_3.0_43650-0200_1x02_P3.00mm_Horizontal; Manufacturer_Part_Number 43650-0200
J3: 7V connector; Molex_Micro-Fit_3.0_43650-0200_1x02_P3.00mm_Horizontal; Manufacturer_Part_Number 43650-0200
J4: D-sub input; AMPHENOL_LD15P33E4GX00LF; Manufacturer_Part_Number LD15P33E4GX00LF
J5: D-sub output; AMPHENOL_LD15S33E4GV00LF; Manufacturer_Part_Number LD15S33E4GV00LF
L1_1: 2.2uH; IND_XGL1010-222MED; Manufacturer_Part_Number XGL1010-222MED
L1_2, L1_3: 3.3uH; IND_XGL1010-222MED; Manufacturer_Part_Number XGL1010-332MED
LF1: 100uH; INDPM235220X1300N; Manufacturer_Part_Number SRP2313AA-101M
R1_1, R1_2, R1_3: 3.32M; R_0603_1608Metric; Manufacturer_Part_Number CRCW06033M32FKEA
R2_1: 1.5M; R_0603_1608Metric; Manufacturer_Part_Number CRCW06031M50FKEA
R2_2: 825k; R_0603_1608Metric; Manufacturer_Part_Number CRCW0603825KFKEA
R2_3: 604k; R_0603_1608Metric; Manufacturer_Part_Number CRCW0603604KFKEA
R3_1: 158k; R_0603_1608Metric; Manufacturer_Part_Number CRCW0603158KFKEA
R3_2: 249k; R_0603_1608Metric; Manufacturer_Part_Number CRCW0603249KFKEA
R3_3: 105k; R_0603_1608Metric; Manufacturer_Part_Number CRCW0603105KFKEA
R4_1: 34.8k; R_0603_1608Metric; Manufacturer_Part_Number CRCW060334K8FKEA
R4_2: 34k; R_0603_1608Metric; Manufacturer_Part_Number CRCW060334K0FKEA
R4_3: 9.76k; R_0603_1608Metric; Manufacturer_Part_Number CRCW06039K76FKEA
R5_1, R5_2, R5_3: 75k; R_0603_1608Metric; Manufacturer_Part_Number CRCW060375K0FKEA
R6_1, R6_2, R6_3: 20k; R_0603_1608Metric; Manufacturer_Part_Number CRCW060320K0FKEA
RLED_1: 1k; R_0603_1608Metric; Manufacturer_Part_Number ERJ-PA3J102V
RLED_2: 604R; R_0603_1608Metric; Manufacturer_Part_Number ERJ-PA3D6040V
RLED_3: 261R; R_0603_1608Metric; Manufacturer_Part_Number ERJ-PA3F2610V
RO1, RO3, RO5: 1k; R_0603_1608Metric; Manufacturer_Part_Number ERJ-PA3J102V
RO2, RO4, RO6: 3k3; R_0603_1608Metric; Manufacturer_Part_Number ERJ-PA3J332V
TP1: TestPoint 7V; TestPoint_Pad_D1.0mm
TP2: TestPoint 5V; TestPoint_Pad_D1.0mm
TP3: TestPoint 3.3V; TestPoint_Pad_D1.0mm
TP4: TestPoint_GND; TestPoint_Plated_Hole_D3.0mm
U1, U2, U3: VO615A-4; DIP-4_W10.16mm; Manufacturer_Part_Number VO615A-4
U4: BME280; Bosch_LGA-8_2.5x2.5mm_P0.65mm_ClockwisePinNumbering; Manufacturer_Part_Number BME280

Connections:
+3.3V: C5_1.2, C5_2.2, C5_3.2, CD_1.1, CD_2.1, IC1.11 (EXTVCC), J1.2, L1_1.2, R3_1.1, RLED_3.1, RO2.2, RO4.2, RO6.2, TP3.1 (1_1), U4.6 (VDDIO), U4.8 (VDD)
+5V: C5_4.2, C5_5.2, C5_6.2, IC2.11 (EXTVCC), J2.2, L1_2.2, R3_2.1, RLED_2.1, TP2.1 (1_1)
+7V: C5_7.2, C5_8.2, C5_9.2, IC3.11 (EXTVCC), J3.2, L1_3.2, R3_3.1, RLED_1.1, TP1.1 (1_1)
/EXP_IN+: CFT1.1, J4.13
/EXP_IN-: CFT3.1, J4.14
/EXP_OUT+: CFT2.1, J4.6
/EXP_OUT-: CFT4.1, J4.7
/FB_3V3: IC1.12 (FB_1), IC1.25 (FB_2), R3_1.2, R4_1.1
/FB_5V: IC2.12 (FB_1), IC2.25 (FB_2), R3_2.2, R4_2.1
/FB_7V: IC3.12 (FB_1), IC3.25 (FB_2), R3_3.2, R4_3.1
/IN+: CFT1.3, J5.13
/IN-: CFT3.3, J5.14
/LO: J4.5, U3.2
/LO_Opt: J5.5, RO6.1, U3.4
/OUT+: CFT2.3, J5.6
/OUT-: CFT4.3, J5.7
/SODS: J4.3, U1.2
/SODS_Opt: J5.3, RO2.1, U1.4
/SOE: J4.4, U2.2
/SOE_Opt: J5.4, RO4.1, U2.4
/SPI_CS: J5.10, U4.2 (CSB)
/SPI_MISO: J5.2, U4.5 (SDO)
/SPI_MOSI: J5.9, U4.3 (SDI)
/SPI_SCK: J5.1, U4.4 (SCK)
GND: C1_1.2, C1_2.2, C1_3.2, C1_4.2, C1_5.2, C1_6.2, C1_7.2, C1_8.2, C1_9.2, C1_10.2, C1_11.2, C1_12.2, C1_13.2, C1_14.2, C1_15.2, C1_16.2, C1_17.2, C1_18.2, C2_1.2, C2_2.2, C2_3.2, C3_1.2, C3_2.2, C3_3.2, C5_1.1, C5_2.1, C5_3.1, C5_4.1, C5_5.1, C5_6.1, C5_7.1, C5_8.1, C5_9.1, CD_1.2, CD_2.2, CF1.2, CFT1.2, CFT2.2, CFT3.2, CFT4.2, D1.1 (K), D2.1 (K), D3.1 (K), FL1.4, IC1.4 (PGND_1), IC1.5 (PGND_2), IC1.7 (PGND_3), IC1.8 (PGND_4), IC1.15 (MODE/SYNC), IC1.17 (SGND), IC1.21 (PGND_5), IC1.22 (PGND_6), IC1.23 (PGND_7), IC1.24 (PGND_8), IC2.4 (PGND_1), IC2.5 (PGND_2), IC2.7 (PGND_3), IC2.8 (PGND_4), IC2.15 (MODE/SYNC), IC2.17 (SGND), IC2.21 (PGND_5), IC2.22 (PGND_6), IC2.23 (PGND_7), IC2.24 (PGND_8), IC3.4 (PGND_1), IC3.5 (PGND_2), IC3.7 (PGND_3), IC3.8 (PGND_4), IC3.15 (MODE/SYNC), IC3.17 (SGND), IC3.21 (PGND_5), IC3.22 (PGND_6), IC3.23 (PGND_7), IC3.24 (PGND_8), J1.1, J2.1, J3.1, J5.8, J5.15, R2_1.2, R2_2.2, R2_3.2, R4_1.2, R4_2.2, R4_3.2, R5_1.2, R5_2.2, R5_3.2, R6_1.2, R6_2.2, R6_3.2, TP4.1 (1_1), U1.3, U2.3, U3.3, U4.1 (GND), U4.7 (GND)
GNDREXUS: FL1.3, J4.8, J4.15
unnamed: CF1.1, FL1.2, LF1.1
unnamed: D1.2 (A), RLED_1.2
unnamed: D2.2 (A), RLED_2.2
unnamed: D3.2 (A), RLED_3.2
unnamed: C4_1.1, IC1.1 (BST)
unnamed: IC1.10 (EN/UVLO), R1_1.2, R2_1.1
unnamed: C3_1.1, IC1.18 (INTVCC_1), IC1.20 (INTVCC_2)
unnamed: C4_1.2, IC1.2 (LX_1)
unnamed: IC1.6 (LX_2), L1_1.1
unnamed: IC1.13 (RT), R5_1.1
unnamed: C2_1.1, IC1.14 (SS)
unnamed: IC1.16 (~RESET/TJ), R6_1.1
unnamed: C4_2.1, IC2.1 (BST)
unnamed: IC2.10 (EN/UVLO), R1_2.2, R2_2.1
unnamed: C3_2.1, IC2.18 (INTVCC_1), IC2.20 (INTVCC_2)
unnamed: C4_2.2, IC2.2 (LX_1)
unnamed: IC2.6 (LX_2), L1_2.1
unnamed: IC2.13 (RT), R5_2.1
unnamed: C2_2.1, IC2.14 (SS)
unnamed: IC2.16 (~RESET/TJ), R6_2.1
unnamed: C4_3.1, IC3.1 (BST)
unnamed: IC3.10 (EN/UVLO), R1_3.2, R2_3.1
unnamed: C3_3.1, IC3.18 (INTVCC_1), IC3.20 (INTVCC_2)
unnamed: C4_3.2, IC3.2 (LX_1)
unnamed: IC3.6 (LX_2), L1_3.1
unnamed: IC3.13 (RT), R5_3.1
unnamed: C2_3.1, IC3.14 (SS)
unnamed: IC3.16 (~RESET/TJ), R6_3.1
unnamed: RO1.2, U1.1
unnamed: RO3.2, U2.1
unnamed: RO5.2, U3.1
VIN: C1_1.1, C1_2.1, C1_3.1, C1_4.1, C1_5.1, C1_6.1, C1_7.1, C1_8.1, C1_9.1, C1_10.1, C1_11.1, C1_12.1, C1_13.1, C1_14.1, C1_15.1, C1_16.1, C1_17.1, C1_18.1, IC1.3 (IN_1), IC1.9 (IN_2), IC1.19 (EP), IC2.3 (IN_1), IC2.9 (IN_2), IC2.19 (EP), IC3.3 (IN_1), IC3.9 (IN_2), IC3.19 (EP), LF1.2, R1_1.1, R1_2.1, R1_3.1, RO1.1, RO3.1, RO5.1
VREXUS: FL1.1, J4.1, J4.9

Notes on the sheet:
Temp/Press/Hum
3.3V
Input and output connectors
Power LEDs and TPs


Board: 4 copper layers, 100.0 x 100.0 mm, 94 parts (0 on the bottom side), 59 nets.

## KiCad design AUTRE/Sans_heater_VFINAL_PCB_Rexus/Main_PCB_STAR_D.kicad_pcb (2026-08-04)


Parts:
AE1: Antenna_Chip; U.FL_Molex_MCRF_73412-0110_Vertical
C1, C6, C10: 1uF 0402; C_0402_1005Metric
C2, C4: 12pF 0402; C_0402_1005Metric
C3: 10uF 0402; C_0402_1005Metric
C5, C7, C9, C15, C17, C20, C21: 100nF 0402; C_0402_1005Metric
C8: 10nF 0402; C_0402_1005Metric
C11, C13: 0.1uF 0402; C_0402_1005Metric
C14: 15pF 0402; C_0402_1005Metric
C25, C26: 0.1uF; C_0402_1005Metric
D1: MBR0520; D_SOD-123
D2, D3, D4: KT-0805Y; LED_0805_2012Metric
H1, H2, H3, H4: MountingHole_Pad; MountingHole_4.3mm_M4_DIN965_Pad
IC2: W25Q01JVZEIQ; WSON-8-1EP_6x5mm_P1.27mm_EP3.4x4.3mm; Manufacturer_Part_Number W25Q01JVZEIQ; Mouser Part Number 454-W25Q01JVZEIQ
J1: Conn_01x05_Pin; JST_EH_S5B-EH_1x05_P2.50mm_Horizontal
J2: Conn_01x09; JST_GH_BM09B-GHS-TBT_1x09-1MP_P1.25mm_Vertical
J3: Conn_01x04_Pin; JST_EH_S4B-EH_1x04_P2.50mm_Horizontal
J4, J7: Conn_01x06_Pin; JST_EH_S6B-EH_1x06_P2.50mm_Horizontal
J10: TYPE-C 16PIN 2MD(073); USB_C_Receptacle_GCT_USB4105-xx-A_16P_TopMnt_Horizontal
J11: Conn_01x03; JST_EH_S3B-EH_1x03_P2.50mm_Horizontal
J14: Conn_01x04; JST_PH_S4B-PH-K_1x04_P2.00mm_Horizontal
L1: 2.0nH 0402; L_0402_1005Metric
L3: 4.7nH 0402; L_0402_1005Metric
R1, R5: 10kR 0402; R_0402_1005Metric
R2: 2R 0402; R_0402_1005Metric
R4: 1kR 0402; R_0402_1005Metric
R14, R15: 5.1kR 0402; R_0402_1005Metric
R16, R17: 22R 0402; R_0402_1005Metric
R18, R19: 2kR 0402; R_0402_1005Metric
R_ADC_POT1: 1kR 0402; R_0402_1005Metric
R_I2C_SCL1, R_I2C_SCL2: 4K7 0402; R_0402_1005Metric
SW1, SW2: SW_SPST; SW_Tactile_SPST_NO_Straight_CK_PTS636Sx25SMTRLFS
TP2, TP3, TP4, TP5, TP6, TP7, TP8, TP9, TP10, TP11, TP12, TP13, TP14, TP15, TP16, TP18: TestPoint; TestPoint_Pad_1.0x1.0mm
U1: ESP32-S3; QFN-56-1EP_7x7mm_P0.4mm_EP4x4mm
U2: BME280; Bosch_LGA-8_2.5x2.5mm_P0.65mm_ClockwisePinNumbering
U4: LSM6DSM; LGA-14_3x2.5mm_P0.5mm_LayoutBorder3x4y
Y1: 40MHz 3225 9pF; Crystal_SMD_3225-4Pin_3.2x2.5mm

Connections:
+3.3V: C1.1, C3.1, C5.2, C6.1, C8.1, C9.1, C10.1, C11.1, C13.1, C20.2, C21.2, C25.1, C26.1, IC2.8 (VCC), J1.2, J4.3, J7.1, J11.1, L1.1, R1.1, R4.1, R5.1, R_I2C_SCL1.2, R_I2C_SCL2.2, U1.20 (VDD3P3_RTC), U1.29 (VDD_SPI), U1.46 (VDD3P3_CPU), U1.55 (VDDA), U1.56 (VDDA), U2.6 (VDDIO), U2.8 (VDD), U4.5 (VDDIO), U4.8 (VDD); also elsewhere on the board
+5V: D1.1 (K), R18.1; also elsewhere on the board
+7V: R19.1; also elsewhere on the board
/FLASH-CLK: IC2.6 (CLK), U1.33 (SPICLK)
/FLASH-CS0: IC2.1 (~CS), U1.32 (SPICS0)
/FLASH-D: IC2.5 (DI_(IO0)), U1.35 (SPID)
/FLASH-HD: IC2.7 (~HOLD_OR_/RESET_(IO3)), U1.30 (SPIHD)
/FLASH-Q: IC2.2 (DO_(IO1)), U1.34 (SPIQ)
/FLASH-WP: IC2.3 (~WP_(IO2)), U1.31 (SPIWP)
/USB-Net-D+: J10.A6 (D+), J10.B6 (D+), R17.1
/USB-Net-D-: J10.A7 (D-), J10.B7 (D-), R16.1
CS_ABP: J1.5, U1.14 (GPIO9)
CS_BME280: U1.15 (GPIO10), U2.2 (CSB)
CS_EXTERNAL_BME280: J7.6, U1.16 (GPIO11)
CS_LSM6DSM: U1.17 (GPIO12), U4.12 (CS)
CS_MAX31865: U1.27 (GPIO21); also elsewhere on the board
CS_RASP: J3.1, U1.39 (GPIO34)
DIR_M1: U1.11 (GPIO6); also elsewhere on the board
EN_STEPPERS: U1.13 (GPIO8)
ESP_32_DI: U1.50 (U0RXD); also elsewhere on the board
ESP_32_RO: U1.49 (U0TXD); also elsewhere on the board
EXP_IN+: J2.3, TP13.1 (1_1); also elsewhere on the board
EXP_IN-: J2.4, TP14.1 (1_1); also elsewhere on the board
EXP_OUT+: J2.2, TP12.1 (1_1); also elsewhere on the board
EXP_OUT-: J2.1, TP11.1 (1_1); also elsewhere on the board
GND: AE1.2 (PCB_Trace), C1.2, C2.2, C3.2, C4.2, C5.1, C6.2, C7.1, C8.2, C9.2, C10.2, C11.2, C13.2, C14.2, C15.2, C17.2, C20.1, C21.1, C25.2, C26.2, D2.1 (K), D3.1 (K), D4.1 (K), H1.1 (1_1), H2.1 (1_1), H3.1 (1_1), H4.1 (1_1), IC2.4 (GND), IC2.9 (EP), J1.1, J2.8, J2.9, J4.4, J7.2, J10.A1 (GND), J10.A12 (GND), J10.B1 (GND), J10.B12 (GND), J10.S1 (SHIELD), J11.3, J14.1, R14.2, R15.2, SW1.2 (B), SW2.2 (B), TP18.1 (1_1), U1.57 (GND), U2.1 (GND), U2.7 (GND), U4.6 (GND), U4.7 (GND), Y1.2, Y1.4; also elsewhere on the board
GPIO_ADC: C17.1, R_ADC_POT1.2, U1.9 (GPIO4)
HEATER1_EN: J14.2, U1.38 (GPIO33)
HEATER2_EN: J14.3, U1.42 (GPIO37)
HEATER3_EN: J14.4, U1.43 (GPIO38)
I2C_SCL: J4.5, R_I2C_SCL2.1, TP7.1 (1_1), U1.8 (GPIO3)
I2C_SDA: J4.2, R_I2C_SCL1.1, TP8.1 (1_1), U1.12 (GPIO7)
INT_LSM6DSM: U1.24 (GPIO18), U4.4 (INT1)
LO_IN: J2.5, TP15.1 (1_1), U1.6 (GPIO1)
unnamed: AE1.1 (FEED), C14.1, L3.2
unnamed: C2.1, R2.1, TP2.1 (1_1), Y1.1
unnamed: C7.2, L1.2, U1.2 (VDD3P3), U1.3 (VDD3P3)
unnamed: D1.2 (A), J10.A4 (VBUS), J10.A9 (VBUS), J10.B4 (VBUS), J10.B9 (VBUS)
unnamed: D2.2 (A), R4.2
unnamed: D3.2 (A), R18.2
unnamed: D4.2 (A), R19.2
unnamed: J10.A5 (CC1), R15.1
unnamed: J10.B5 (CC2), R14.1
unnamed: J11.2, R_ADC_POT1.1
unnamed: R1.2, SW1.1 (A), U1.5 (GPIO0)
unnamed: C15.1, R5.2, SW2.1 (A), U1.4 (CHIP_PU)
unnamed: L3.1, U1.1 (LNA_IN)
unnamed: C4.1, TP3.1 (1_1), U1.53 (XTAL_N), Y1.3
unnamed: R2.2, U1.54 (XTAL_P)
RASP_CLK: J3.2, U1.40 (GPIO35)
RASP_MISO: J3.4, U1.52 (GPIO46)
RASP_MOSI: J3.3, U1.41 (GPIO36)
SODS_IN: J2.7, TP5.1 (1_1), U1.19 (GPIO14)
SOE_IN: J2.6, TP16.1 (1_1), U1.7 (GPIO2)
SPI_MISO: J1.4, J7.5, U1.51 (GPIO45), U2.5 (SDO), U4.1 (SDO/SA0); also elsewhere on the board
SPI_MOSI: J7.4, TP6.1 (1_1), U1.23 (GPIO17), U2.3 (SDI), U4.14 (SDA); also elsewhere on the board
SPI_SCK: J1.3, J7.3, TP4.1 (1_1), U1.18 (GPIO13), U2.4 (SCK), U4.13 (SCL); also elsewhere on the board
STEP_M1: U1.10 (GPIO5); also elsewhere on the board
USB-D+: R17.2, TP10.1 (1_1), U1.26 (GPIO20/USB_D+)
USB-D-: R16.2, TP9.1 (1_1), U1.25 (GPIO19/USB_D-)

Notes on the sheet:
J_ABP
VDD3P3_CPU
External_BME280
Clock
VDD3P3_RTC
BOOT
VDDA
SLF3S
RESET
BME280
FLASH
VDD3P3
Connector to D-sub
MAX31865ATP+
Leds debug
Test Points
LSM6DSM
VDD_SPI
Potentiometer
USB-C


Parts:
C23, C28, C31: 10uF 0603; C_0603_1608Metric
C27, C30, C33: 100nF 0402; C_0402_1005Metric
J6, J12, J13: Conn_01x02_Pin; AMASS_XT30U-F_1x02_P5.0mm_Vertical

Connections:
+3.3V: C28.1, C30.1, J12.2; also elsewhere on the board
+5V: C31.1, C33.1, J13.2; also elsewhere on the board
+7V: C23.1, C27.1, J6.2; also elsewhere on the board
GND: C23.2, C27.2, C28.2, C30.2, C31.2, C33.2, J6.1, J12.1, J13.1; also elsewhere on the board

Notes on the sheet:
Power Unit Converter to Main PCB (3V3 and 5V)


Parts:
C18, C19, C24: 100nF 0402; C_0402_1005Metric
IC1: MAX31865ATP+; QFN65P500X500X80-21N; Manufacturer_Part_Number MAX31865ATP+; Mouser Part Number 700-MAX31865ATP+
J8: Conn_01x02; JST_EH_S2B-EH_1x02_P2.50mm_Horizontal
R7: 400R 0402; R_0402_1005Metric

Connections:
+3.3V: C18.2, C19.1, IC1.19 (DVDD), IC1.20 (VDD); also elsewhere on the board
CS_MAX31865: IC1.13 (~CS); also elsewhere on the board
GND: C18.1, C19.2, IC1.6 (FORCE2), IC1.10 (GND2), IC1.15 (DGND), IC1.16 (GND1), IC1.21 (EP); also elsewhere on the board
unnamed: IC1.1 (BIAS), IC1.2 (REFIN+), R7.1
unnamed: C24.1, IC1.5 (FORCE+), IC1.7 (RTDIN+), J8.2
unnamed: C24.2, IC1.8 (RTDIN-), IC1.9 (FORCE-), J8.1
unnamed: IC1.3 (REFIN-), IC1.4 (ISENSOR), R7.2
SPI_MISO: IC1.14 (SDO); also elsewhere on the board
SPI_MOSI: IC1.11 (SDI); also elsewhere on the board
SPI_SCK: IC1.12 (SCLK); also elsewhere on the board


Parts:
C22: 100nF 0402; C_0402_1005Metric
IC3: ISL83491IBZ-T; SOIC127P600X175-14N; Manufacturer_Part_Number ISL83491IBZ-T; Mouser Part Number 968-ISL83491IBZ-T
R10: 120R 0402; R_0402_1005Metric

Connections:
+3.3V: C22.1, IC3.4 (DE), IC3.13 (VCC_1), IC3.14 (VCC_2); also elsewhere on the board
ESP_32_DI: IC3.5 (DI); also elsewhere on the board
ESP_32_RO: IC3.2 (RO); also elsewhere on the board
EXP_IN+: IC3.12 (A), R10.1; also elsewhere on the board
EXP_IN-: IC3.11 (B), R10.2; also elsewhere on the board
EXP_OUT+: IC3.9 (Y); also elsewhere on the board
EXP_OUT-: IC3.10 (Z); also elsewhere on the board
GND: C22.2, IC3.3 (~RE), IC3.6 (GND_1), IC3.7 (GND_2); also elsewhere on the board


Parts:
C12: 10nF 0603; C_0402_1005Metric
C16: 2.2uF 0603; C_0402_1005Metric
IC4: DRV8834PWP; SOP65P640X120-25N; Manufacturer_Part_Number DRV8834PWP; Mouser Part Number 595-DRV8834PWP
J5: Conn_01x04; JST_PH_S4B-PH-K_1x04_P2.00mm_Horizontal
R3: 47kR 0402; R_0402_1005Metric
R6, R8: 51kR 0402; R_0402_1005Metric
R9, R11: 0.2R 1206; R_0402_1005Metric
R12: 10kR 0402; R_0402_1005Metric
R13: 22kR 0402; R_0402_1005Metric
TP1: TestPoint; TestPoint_Pad_1.0x1.0mm

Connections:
+7V: C12.1, IC4.18 (VM_1), IC4.19 (VM_2), R3.2; also elsewhere on the board
DIR_M1: IC4.12 (DIR_/_BPHASE); also elsewhere on the board
GND: C16.2, IC4.10 (NENBL_/_AENBL), IC4.21 (GND_1), IC4.25 (GND_2), R6.1, R8.1, R9.1, R11.1, R12.2; also elsewhere on the board
MOTOR_A1: IC4.4 (AOUT1), J5.1
MOTOR_A2: IC4.6 (AOUT2), J5.2
MOTOR_B1: IC4.9 (BOUT1), J5.3
MOTOR_B2: IC4.7 (BOUT2), J5.4
unnamed: IC4.3 (ADECAY), R8.2
unnamed: IC4.5 (AISEN), R9.2
unnamed: IC4.22 (AVREF), IC4.23 (BVREF), R12.1, R13.2, TP1.1 (1_1)
unnamed: IC4.2 (BDECAY), R6.2
unnamed: IC4.8 (BISEN), R11.2
unnamed: C16.1, IC4.13 (M0_/_APHASE), IC4.14 (M1), IC4.15 (CONFIG), IC4.20 (VINT)
unnamed: IC4.1 (NSLEEP), R3.1
unnamed: C12.2, IC4.17 (VCP)
unnamed: IC4.24 (VREFO), R13.1
STEP_M1: IC4.11 (STEP_/_BENBL); also elsewhere on the board



Board: 4 copper layers, 90.0 x 40.0 mm, 104 parts (8 on the bottom side), 76 nets.

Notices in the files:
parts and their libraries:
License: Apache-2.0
